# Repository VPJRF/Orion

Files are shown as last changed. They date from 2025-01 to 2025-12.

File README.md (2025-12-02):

# Orion
*Een slim hulpmiddel dat de nachtrust en gemoedsrust van een mantelzorger van een persoon met dementie verbetert, door de nachtelijke oriëntatie in ruimte en tijd en de slaapkwaliteit van de persoon met dementie te ondersteunen.*

*Projectteam: Elias Verdegem; Viktor Fabry*

23/05/2025

`PD` persoon met dementie <br>
`MZ` mantelzorger (bv. partner) <br>
`PZ` professionele zorgverlener <br>
`IZ` informele zorgverlener (bv. familielid)

## Samenvatting

_Dit project richt zich op het probleem van **verstoorde dag-nachtritmes bij mensen met dementie**, wat zowel hun slaap als de nachtrust van hun verzorgers verstoort._

Het probleem is geanalyseerd door middel van **bevragingen en observaties**, waarbij de verschillende aspecten en gradaties zijn geïdentificeerd. Vervolgens is met behulp van **vijf iteraties aan prototypes** onderzocht hoe het zintuiglijke spectrum optimaal benut kan worden om de PD in zijn zelfstandigheid te ondersteunen.

Een combinatie van **visuele en auditieve prikkels** op strategische plaatsen doorheen de nachthal **begeleidt de PD bij een nachtelijk toiletbezoek** en **voorkomt het mogelijks daarop volgende nachtelijke dwalen**.

> ✨ **_Slimme lampjes verlichten de route en vormen oriëntatiepunten._**<br>
> ⌛ **_Een geruststellende herkenbare stem herinnert aan tijd en nachtrust._**<br>
> ❗ **_Bij afwijking wordt de MZ meteen visueel gewaarschuwd._**

Door de hulp kan de PD ’s nachts zijn plan trekken. De MZ kan met een gerust hart doorslapen.

**_Orion_** *belooft zo de zelfstandigheid van mensen met dementie te bevorderen, hun onrust te verminderen en de belasting voor mantelzorgers te verlichten en maakt zo thuiszorg aangenamer en duurzamer.*

<p align="center">
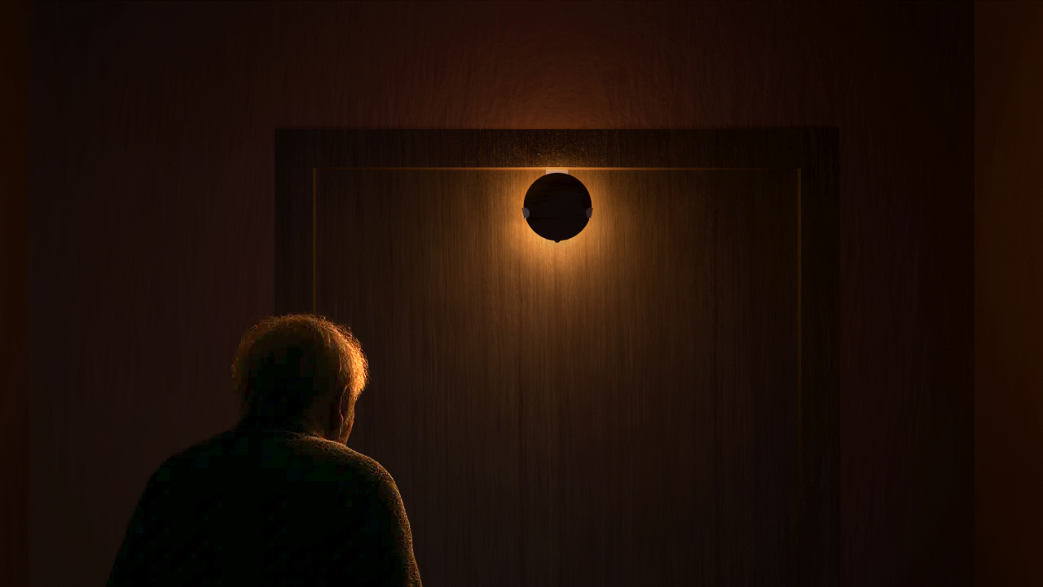
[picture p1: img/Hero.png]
  
</p>

> 🎥 [Ontdek hoe Orion werkt](https://www.youtube.com/watch?v=VIDEO_ID)

## Introductie

> _“Wanneer de nachten te zwaar worden, moeten mantelzorgers [hun partner] loslaten – niet omdat ze willen, maar omdat ze niet meer kunnen.”_ – zorgverlener

Mensen worden steeds ouder. In 2023 in België gemiddeld 82,5 jaar  (PwC, 2024) [^1]. De keerzijde van de medaille is dat hierdoor chronische ouderdomsziektes zoals Alzheimer's vaker voorkomen. **Op vandaag krijgt ongeveer 1 op 5 in de loop van zijn of haar leven een vorm van dementie.** Dementie is een wereldwijd probleem dat 55 miljoen mensen treft en jaarlijks 10 miljoen nieuwe gevallen kent. In België lijden ongeveer 200.000 personen aan een vorm van dementie, en door de vergrijzing wordt verwacht dat dit aantal tegen 2070 zal verdubbelen (Expertisecentrum Dementie, 2021) [^2]. In het toekomstige value based healthcare (VBHC) model (PwC, 2024) [^1] **wordt de zorgverlening verder richting de eerstelijns- en nuldelijnszorg verschoven**. Dit moet onder andere een oplossing bieden aan het groeiende personeelstekort in de gezondheidssector. **Deze evolutie onderstreept het belang van de informele zorgverlener en in het bijzonder de mantelzorger in het geval van zorg voor mensen met dementie.**

**Personen met dementie hebben moeite met een standaard slaappatroon, wat leidt tot nachtelijke onrust en dwalen** (Thomas & Ritter, 2022) [^3]. Dit verstoort niet alleen de nachtrust van de persoon met dementie zelf, maar ook die van hun mantelzorgers, vaak de partner. **Deze aanhoudende belasting kan leiden tot fysieke en emotionele uitputting van de mantelzorger**, wat de beslissing tot een vaste opname in een woonzorgcentrum kan bespoedigen.

**Het doel van dit project is om een oplossing te ontwikkelen die de nachtrust van PD en hun MZ bevordert, zodat thuiszorg langer mogelijk blijft**. Daarbij is het cruciaal om de autonomie van de zorgbehoevende te ondersteunen en de druk op MZ te verlagen. Dit vereist oplossingen die rekening houden met de **uiteenlopende en veranderende cognitieve en zintuiglijke capaciteiten van PD**. De focus ligt op het minimaliseren van nachtelijke interventies en het ondersteunen van een zelfstandig dag-nachtritme. De ontwikkelde oplossing moet bovendien flexibel zijn en ook in een woonzorgcentrum gebruikt kunnen worden om de professionele zorgverleners te ontlasten.

## Methodologie



De methodologie volgt het **triple diamond** ontwerpmodel, bestaande uit vier fasen: **discover**, **define**, **develop** en **deliver**.

In de fase **discover** wordt via een **literature review (N=16)** onderzoek gedaan naar uitdagingen in de zorg voor personen met dementie. Vervolgens vinden **user interviews (N=4)** plaats met mantelzorgers, familieleden en zorgverleners, waarbij gebruik wordt gemaakt van **empathy mapping**. Daarnaast wordt via **ethnography (N=1)** de dagelijkse praktijk geobserveerd in dagverblijf DVC Robijn, afdeling dementie, binnen WZC Sint Eligius. De verzamelde inzichten zijn gestructureerd weergegeven in een **fishbone diagram**, waarbij vooral het verstoorde dag-nachtritme en de daarmee samenhangende belasting voor mantelzorgers naar voren komen als prioritair probleem. Een aanvullend **state of the art**-onderzoek leidt tot het initiële concept van de klinkklok als vertrekpunt voor verdere testen.

Tijdens de **define**-fase worden prototypes iteratief ontwikkeld en geëvalueerd in testwaves, met elk een specifieke focus. In **wave 1** worden **conceptuele prototypes** (klinkklok, vloerlicht, breadcrumbs) onderzocht via **user feedback sessions (N=7)** met mantelzorgers en professionele zorgverleners in Huize Ter Walle, en via **user feedback sessions (N=3)** in DVC Robijn. Nadien wordt een stap teruggenomen met een gerichte **literature review (N=1)** over de problematiek van dwalen en sundowning. In **wave 2** worden de bevindingen toegepast als **feature prototypes** (beacon, breadcrumb, kussen, knuffel) die zich richten op het vaststellen van de featureset via een **evaluation matrix**, met **Wizard of Oz testing (N=3)** bij ouderen met en zonder dementie. Voorafgaand vindt er een ongeplande **user evaluation (N=1)** plaats met een expert in fixatie en valpreventie. De resultaten zijn geprioriteerd volgens de **MoSCoW-methode**, wat resulteert in een productconcept bestaande uit licht en geluid nabij het bed, de slaapkamerdeur en het sanitair, inclusief een feedbacksysteem voor mantelzorgers. Uitdagingen liggen in acceptatie, adaptatie en tijdige implementatie. Opties voor uitbreiding naar andere doelgroepen zijn onderzocht om het product reeds in een vroeg stadium van de ziekte te introduceren.

In de fase **develop** wordt via **CMF prototypes** (vlinderlampjes) de uiteindelijke look & feel bepaald, met behulp van een **interactive survey (N=12)** bij ouderen en ouders van jonge kinderen via **BERT-testing**. In **wave 4** zijn de **UI & UX prototypes** geëvalueerd via **Wizard of Oz testing (N=5)** met het **think aloud protocol**.

De laatste fase **deliver** omvat de evaluatie van volledig autonome prototypes (**wave 5**) als **pilot testing** via een **validation session (N=2)**.

## Discovery

### Doelstellingen

Een goed beeld vormen van wat de ziekte inhoud en de impact op de omgeving.

> ❓**Hoe draag je bij aan het mentaal welzijn van mantelzorgers** door hun tijd besteed aan zorg te optimaliseren?
> -	Welke lasten hebben de grootste impact op de mantelzorgers?
> -	Welke ontlasting heeft de grootste potentiële impact?
> -	Welke technologieën bestaan er?

### Materiaal & methoden

Het onderzoek vat aan met een **literature review (N=16)**. Artikels over het ziektebeeld en technologische vorderingen vormen het referentiekader. In een **technology scan** wordt bestaande technologie verzameld tot een beeld over de “state of the art”. Later in het onderzoek doen ze dienst als **benchmarks** voor de productideeën.

De literatuurstudie wordt gevolgd door **ethnographic fieldwork (N=1)** in de dagopvang in WZC St-Eligius. Het volgen van **a day in the life** van professionele zorgverleners en de gasten verrijkt met **contextual inquiries** worden in **field notes** verzamend. In een **cause-and-effect diagram** diagram worden de conclusies gestructureerd.

Een dieper inzicht in de dagelijkse impact van de ziekte op de naasten in thuissituaties zijn verkregen door **user interviews (N=4)** met eerste- en tweedelijns mantelzorgers. **Habit analysis** van frequente scenario’s en **empathy mapping** van de emotionele impact worden gehanteerd om kerngedachten te capteren.

Om te achterhalen voor welk probleem een oplossing binnen handbereik is, worden de bevindingen in een **feasability-desireabilitydiagram** geordend. Het meest zinvolle probleem wordt in een _how might we_ geformuleerd. **Personas** doen dienst als toetsing tijdens _definition_ fase.

### Resultaten

#### Literature review (N=16)

📄 [Protocol](https://ugentbe-my.sharepoint.com/:b:/g/personal/elias_verdegem_ugent_be/EdiS3hkiKK1MplGdmVTWungBmxVn0FbBp6aX2gbiq4Yjcw?e=3pP9zS)
📄 [Rapport](https://ugentbe-my.sharepoint.com/:b:/g/personal/elias_verdegem_ugent_be/EVpkX9X-c-hKqZcMqP5W1E4BfmoQJAslg8WdfgcqIlADtQ?e=OeRcE2)

Dementie is een complexe ziekte met uiteenlopende symptomen.
-	**Geheugen** en **cognitie** (woordvinding, planning en organisatie, oriëntatie in tijd)
-	**Gedrag** en **karakter** (apathie, agressie, angst, verdriet, kwaadheid)
-	**Functionele tekorten** in het dagelijkse leven (basale activiteiten, complexe activiteiten)

Er is een groeiende erkenning van de waardevolle rol van technologie in de ondersteuning van personen met dementie en hun zorgverleners. De meeste technologieën richten zich op de patiënt zelf.
-	**Communicatie** en **sociale interactie**
-	Fysieke **veiligheid** en **bewegingsvrijheid**
-	**Cognitieve stimulatie** en **geheugenondersteuning**
-	Ondersteuning voor dagelijkse zorgactiviteiten en **zelfredzaamheid**

**Artificiële intelligentie** is een belangrijke trend die hierin nieuwe mogelijkheden biedt. Omwille van de leeftijd en de achteruitgaande cognitieve capaciteiten van het doelpubliek brengt de introductie van nieuwe technologieën enkele belangrijke complexiteiten met zich mee.

#### User interviews (N=4)

📄 [Protocol](https://ugentbe-my.sharepoint.com/:b:/g/personal/elias_verdegem_ugent_be/EcmzMGjfi_pDri7_CiFLg6sBVcVGTVBcUN_csnUy3V1scA?e=q4lqXB)

<p align="left">
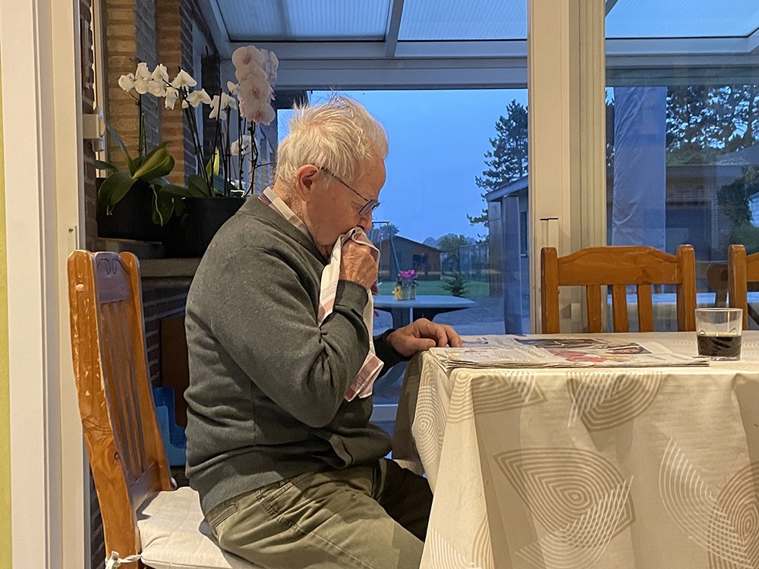
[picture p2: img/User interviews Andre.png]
  
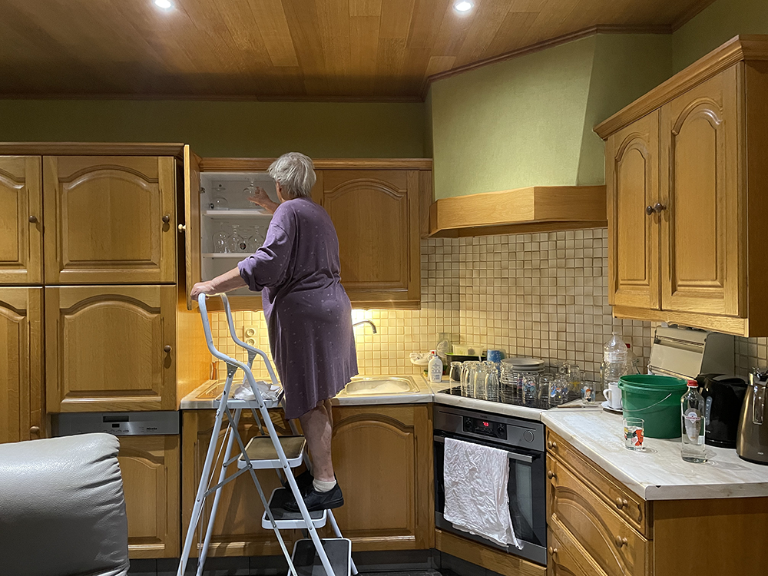
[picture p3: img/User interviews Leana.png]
  
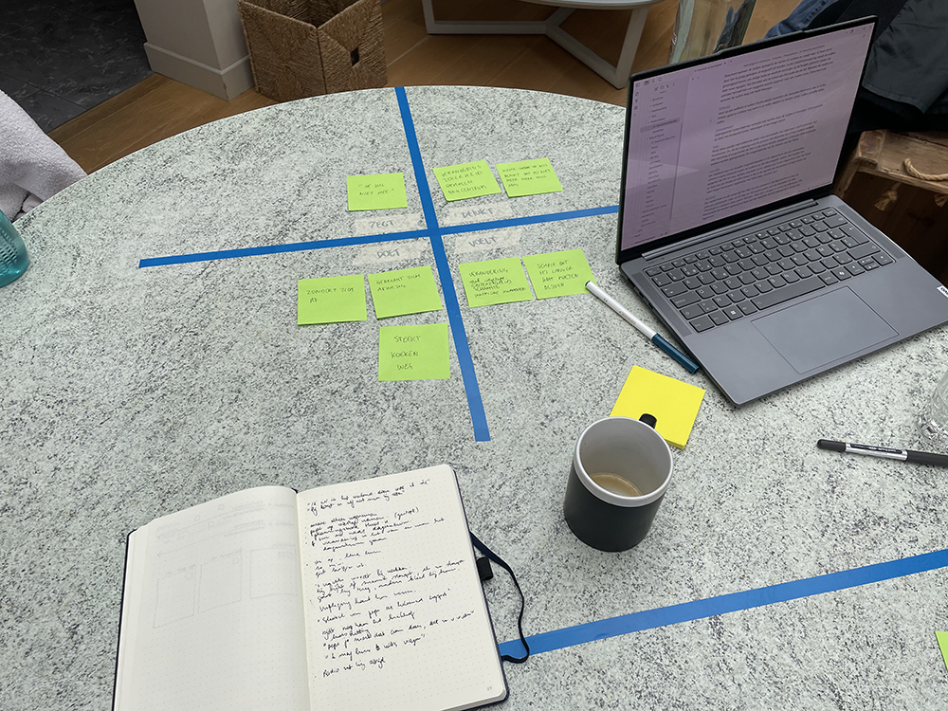
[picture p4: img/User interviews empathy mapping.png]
  
</p>

Wat in de literatuurstudie nog onderbelicht lijkt, maar in de praktijk sterk naar voor komt, zijn de moeilijke nachten.

> _“Zit hij daar midden in de nacht aan de keukentafel, volledig gekleed, z’n krant aan ‘t lezen.”_ – mantelzorger en partner

Mantelzorgers willen de overstap van thuiszorg naar een woonzorgcentrum zo lang mogelijk uitstellen. Uit schrik om gescheiden te zijn, maar ook uit schaamte om te moeten toegeven dat ze het niet meer aankunnen.

> _“Na een week in kortverblijf is hij sterk achteruit gegaan. Sindsdien komt hij er niet meer bij zitten wanneer er bezoek is.”_ – tweedelijn informele zorgverlener (zoon)

#### Ethnography (N=1)

📄 [Protocol](https://ugentbe-my.sharepoint.com/:b:/g/personal/elias_verdegem_ugent_be/EbZtCITc4uJAq0ycfyGaPi8BeBhuUqo_bVPuqhUFXoU3WQ?e=zYbrPR)
📄 [Rapport](https://ugentbe-my.sharepoint.com/:b:/g/personal/elias_verdegem_ugent_be/EUZXoSR17MNIq53AvzIOdvEBZ89_BWPycliHvZ6ZHHcRLg?e=TfPVYO)

<p align="left">
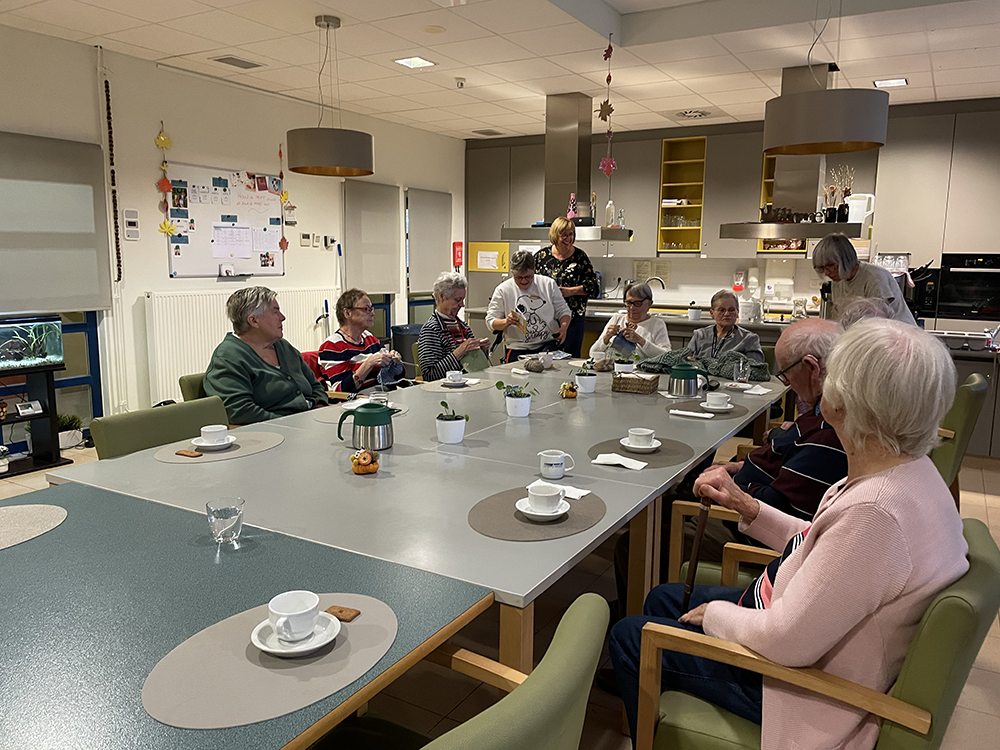
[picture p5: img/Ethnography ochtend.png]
  
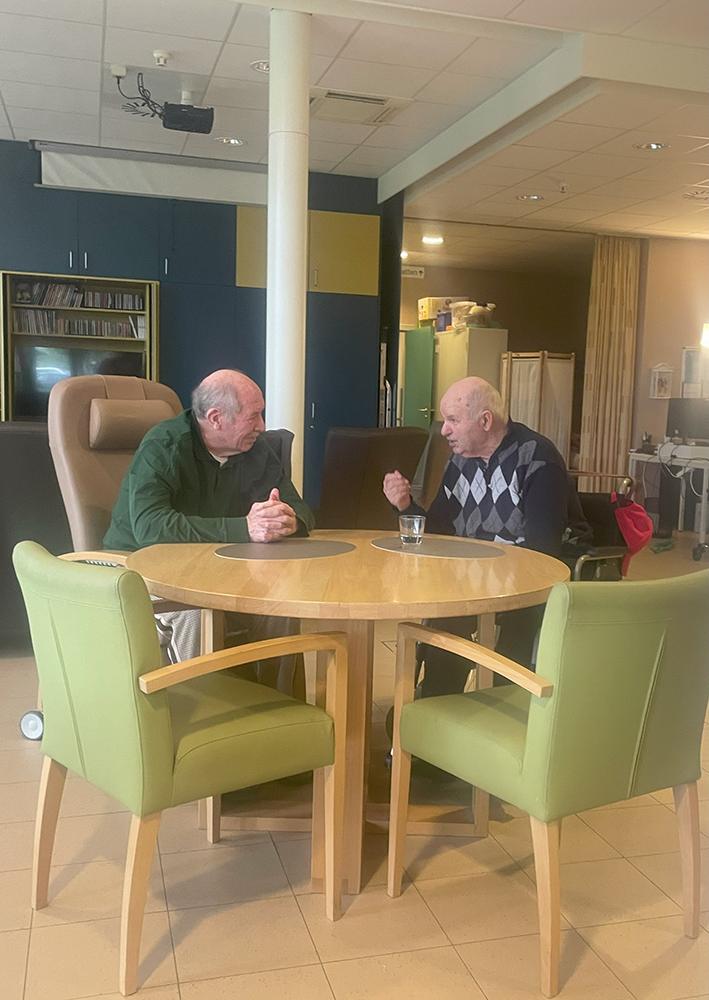
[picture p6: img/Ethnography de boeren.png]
  
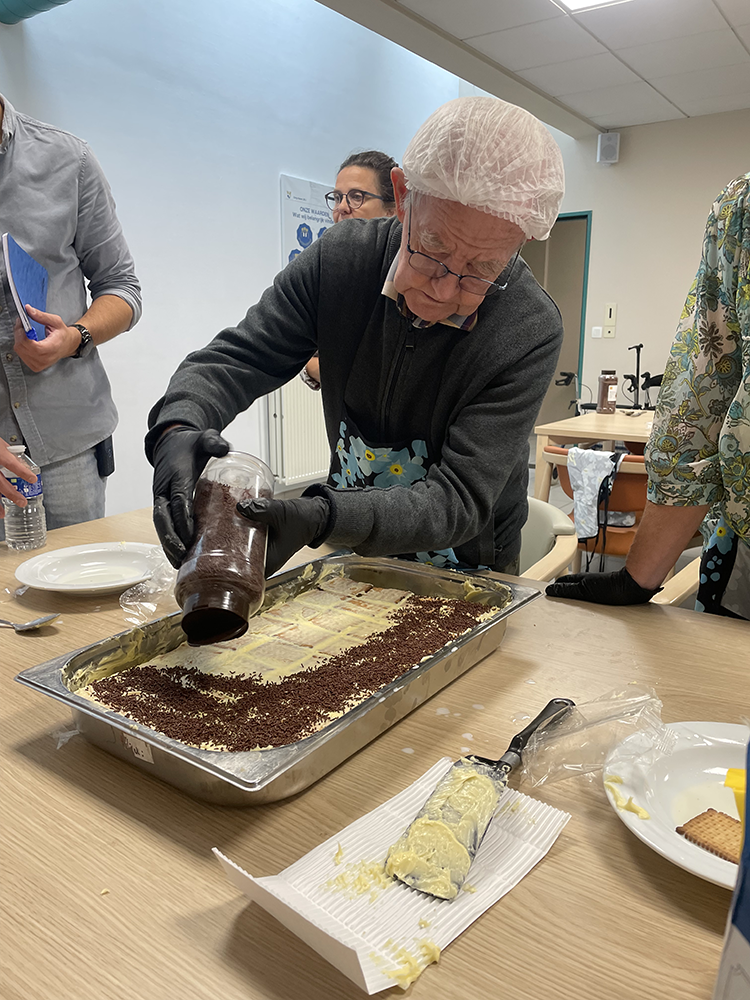
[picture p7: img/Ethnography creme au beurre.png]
  
</p>

Ondanks het personeelstekort wijzen de professionele zorgverleners voornamelijk in de richting van de **mantelzorgers** wanneer het over overbelasting gaat. Ze spelen een cruciale rol doorheen de evolutie van de ziekte. Ze krijgen te kampen met **fysieke**, **emotionele**, **financiële** en **praktische** problemen.
Een gebrek aan **tijd** en **middelen** vormt veelal de onderliggende oorzaak.

> _“Wanneer we dan vragen hoe het met ze gaat, barsten ze in tranen uit.”_ – zorgverlener

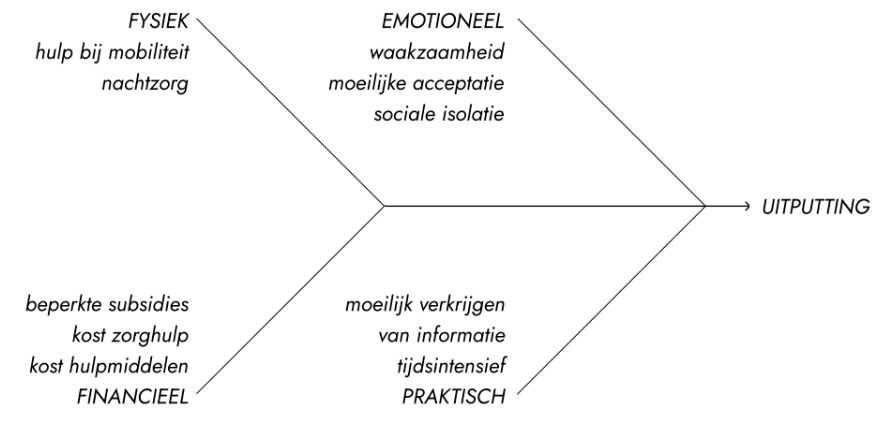
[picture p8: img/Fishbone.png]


Mantelzorgers wijden hun leven vaak volledig aan hun partner met de ziekte toe, ten koste van zichzelf. Liefde ruimt plaats voor gemis, frustratie en schaamte.
Dagcentra of een uitstap met een vrijwilliger of tweede lijn mantelzorger bieden ademruimte. Mantelzorgers hebben deze tijd nodig om van de vaak **korte nachten** en **zware zorgdagen** te recupereren en **sociaal isolement** te vermijden.
<br clear="all">

> _"[…] haar mantelzorger komt haar 's ochtends soms met tranen in de ogen afzetten." ... "Na 16u staat de mantelzorger er opnieuw alleen voor, net wanneer de gasten net heel overprikkeld zijn."_ – zorgverlener

Er is nood aan een oplossing die ook in de overige uren van de dag de autonomie van de zorgbehoevende ondersteunt.
Zowel in woonzorgcentra als in thuissituaties zijn **nachtelijke problemen** zeer uitputtend door de noodzaak voor permanente **waakzaamheid**. **Incontinentie**, **slapeloosheid**, **doolgedrag** en het bijhorende **valrisico** liggen hierbij aan de bron. 

> _"Sommigen zijn het dag-nachtritme volledig kwijt, wat leidt tot doolgedrag. Dan geef je ze slaapmedicatie, maar vergroot hun valneiging."_ – zorgverlener

De zorgbehoevende verhuist vaak stapsgewijs (via **dagverblijf**, **kortverblijf**, **aanleunflat**) van **thuis** naar **vast verblijf**." Dit valt de MZ heel zwaar en introduceert nieuwe verwarring bij de PD door een nieuwe onherkenbare omgeving.

> _”[…] Sociale Dienst merkt dan op dat de mantelzorger het niet meer aankan. […] Ze hebben het gevoel dat ze hun partner dumpen." [...] "Vanaf dan ben je gescheiden.”_ – zorgverlener

### Conclusies & implicaties

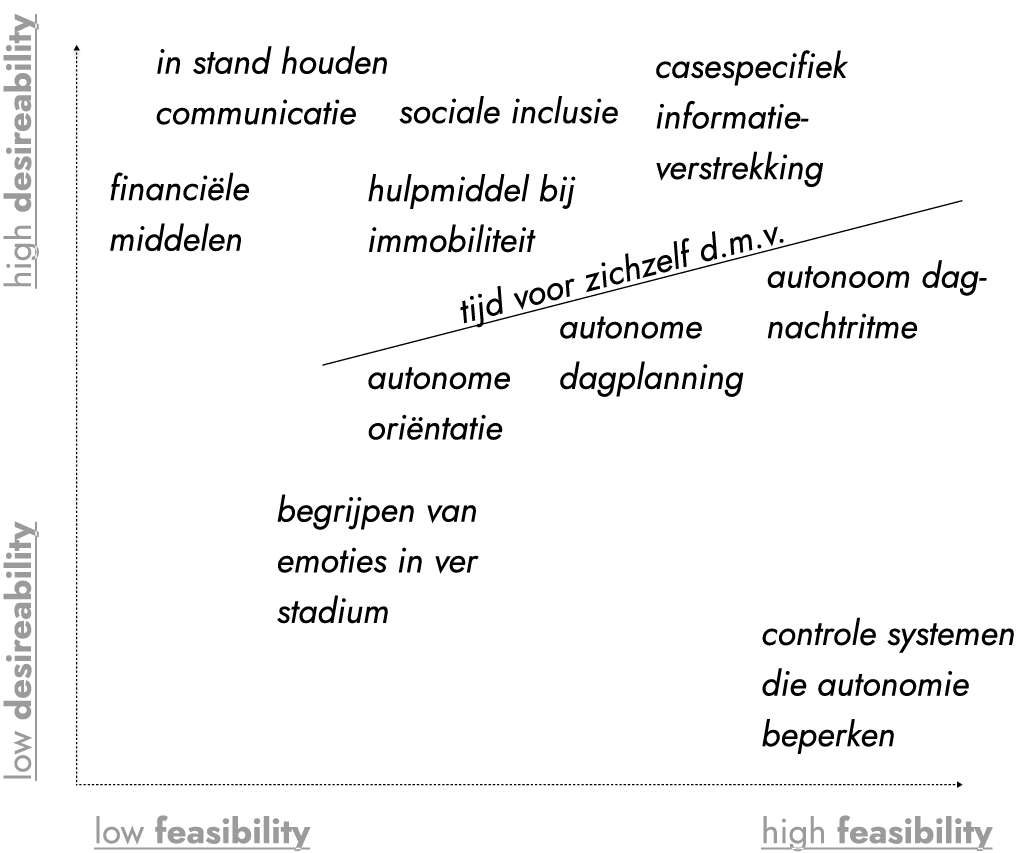
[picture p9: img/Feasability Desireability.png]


MZ van PD dragen een zware, vaak onzichtbare last. Vooral de **nachtelijke zorg** blijkt in de praktijk een cruciale maar onderbelichte bron van uitputting. Het doolgedrag, valgevaar, en het verlies van dag-nachtritme vereisen **permanente waakzaamheid**.

Hoewel bestaande technologieën zich hoofdzakelijk richten op de PD, ligt de **grootste potentiële impact** in oplossingen die de MZ ademruimte gunnen wanneer ze er alleen voor staan. Technologieën die de **autonomie ’s nachts** verhogen en onrust detecteren of vermijden, kunnen niet alleen de draaglast verlichten, maar ook het verblijf thuis aanzienlijk verlengen.

<br clear="all">

>🎯 **_How Might We?_**<br>
> **_Hoe kunnen we ’s nachts de autonomie van personen met dementie ondersteunen en nachtelijke interventies minimaliseren om zo de fysieke en mentale belasting van mantelzorgers te verlichten?_**

<br>

> 📌 **_Design Requirements_**
> - 1\. **Reduceert de noodzaak tot waakzaamheid** en beperkt het aantal nachtelijke interventies van de MZ
> - 2\. **Begeleidt in ruimte en tijd** om aan de zelfstandigheid en eigenwaarden van PD bij te dragen
> - 3\. **Interacties zijn intuïtief en herkenbaar** voor personen met beperkte oriëntatie- of geheugenfunctie
> - 4\. **Reist mee als vertrouwd element** om verwarring bij PD door wijzigende context te verminderen

## Definition I

### Doelstellingen

> ❓ _Hoe draag je bij aan de **nachtelijke zelfstandigheid** van een persoon met dementie?_
> - **Welke situaties** komen het vaakste voor?
> - **Welke interacties** (soort, timing, locatie) zijn intuïtief en behulpzaam?

### Materiaal & methoden

De definition fase wordt gestart met een **design sprint** waarin de **how might we** wordt vertaald in een **innovatrix** en **storyboards**.

Momenteel gebeurt het dat de PD gaat dwalen na op te staan voor een toiletbezoek. De waakzame MZ zal ’s nachts telkens opstaan om de PD opnieuw in slaap te helpen.

<p align="center">
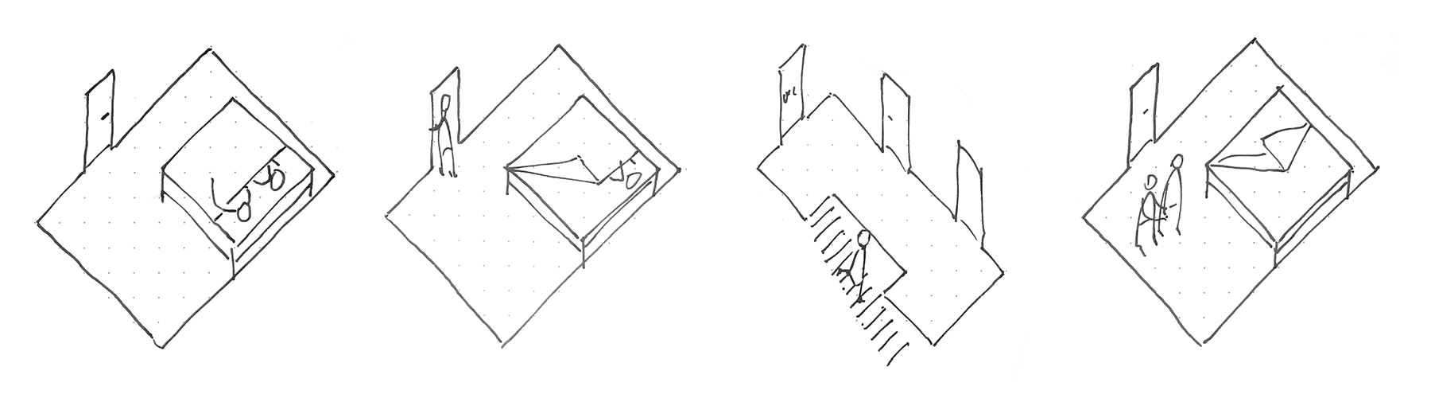
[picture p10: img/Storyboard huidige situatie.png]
  
</p>

De eerste productiteratie is een lichtgevende klink op de slaapkamerdeur. Op basis van kleur wordt onderscheid gemaakt tussen dag en nacht. Een stem biedt tijdgebonden duiding. De klink onderscheidt de kamerdeur van de andere deuren.

<p align="center">
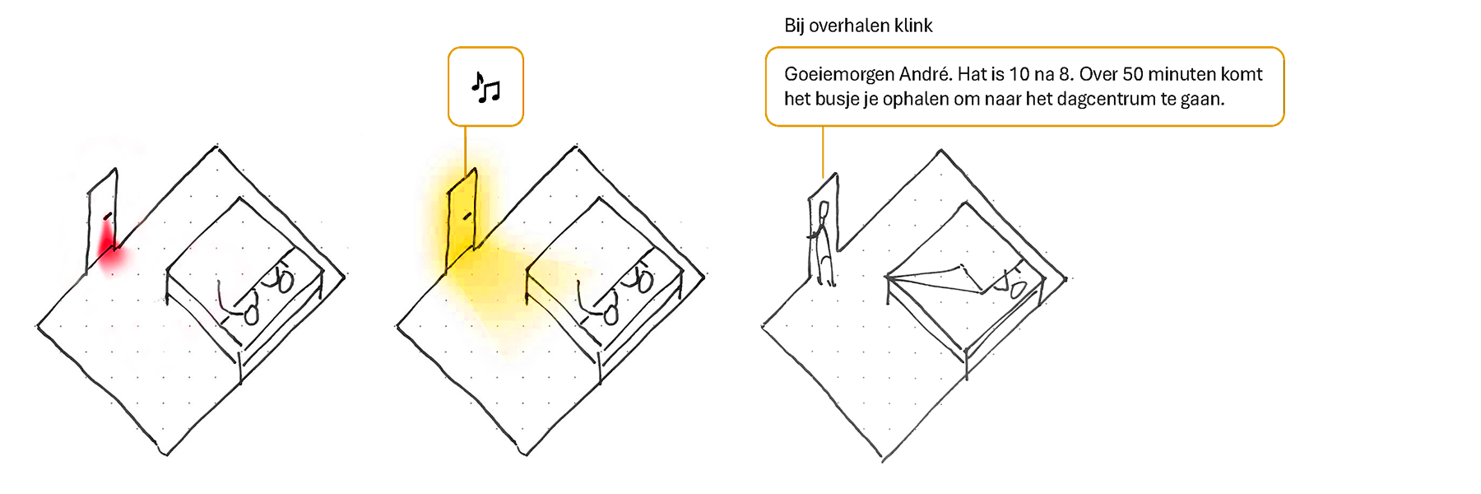
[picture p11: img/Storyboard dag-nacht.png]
  
</p>
<p align="center">
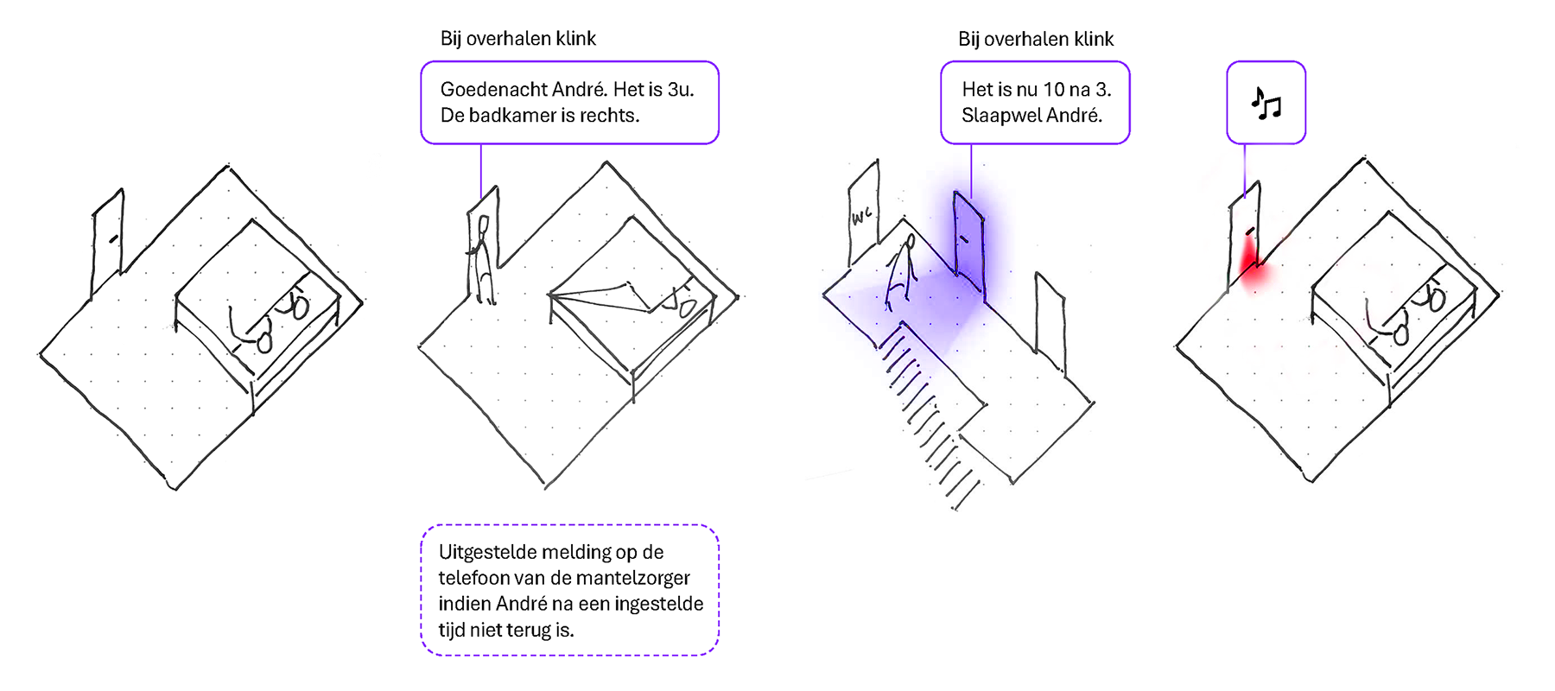
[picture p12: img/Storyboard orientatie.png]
  
</p>

> 🌊 Wave 1 – **conceptuele prototypes** – stimuli
> - **klinkklok**: zoals hierboven beschreven
> - **breadcrumbs**: slimme lichtbronnen die helpen bij veilig en zelfstandig nachtelijk navigeren
> - **vloerlicht**: een vloerdetector die nachtelijk opstaan detecteert en met licht dag-nacht onderscheid maakt en met rustgevend geluid helpt om opnieuw in slaap te vallen

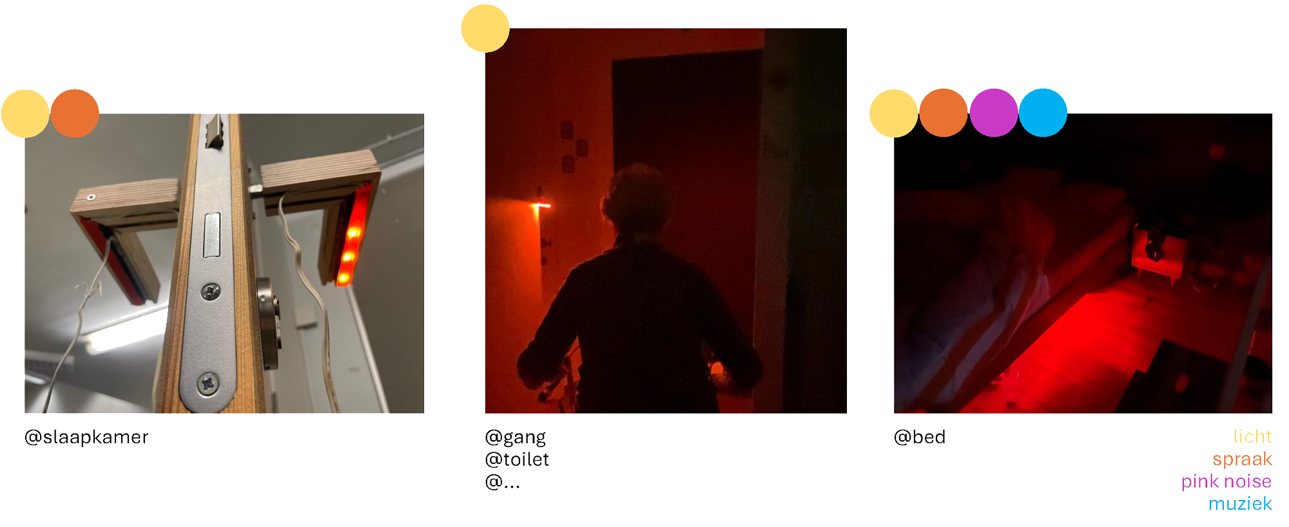
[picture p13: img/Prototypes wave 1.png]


De prototypes worden in een **user feedback sessions (N=10)** in Huize Ter Walle (N=7) en in DVC Robijn (N=3) aan MZs en PZs gedemonstreerd. Er zijn **groepsinterviews** afgenomen en individuele feedback is via een **enquête** verzameld.

### Resultaten

#### User feedback sessions (N=10)

📄 [Protocol](https://ugentbe-my.sharepoint.com/:b:/g/personal/elias_verdegem_ugent_be/EUDGs_sZqw1Cu-SNZ_Z4MUYB4EUygZoMUpzzzmrSuLFlzA?e=GaHmqu)
📄 [Rapport](https://ugentbe-my.sharepoint.com/:b:/g/personal/elias_verdegem_ugent_be/EYPAxhtVcARDhyRcBSE5QyAB_7105NtN1UUdGcgKd0noVQ?e=lRj64M)
📄 [Enquête](https://ugentbe-my.sharepoint.com/:b:/g/personal/elias_verdegem_ugent_be/Ef0tJbKGW_dAtwJForc6fqsBGBC1jhmTAPsUzSV54qDXcQ?e=y3iexh)
📄 [Resultaten](https://ugentbe-my.sharepoint.com/:b:/g/personal/elias_verdegem_ugent_be/ETZRhIU3ZTpDvh90dmZtsAcBM5H1ob_vPhDzmzgHq2v9hA?e=dr1w6v)

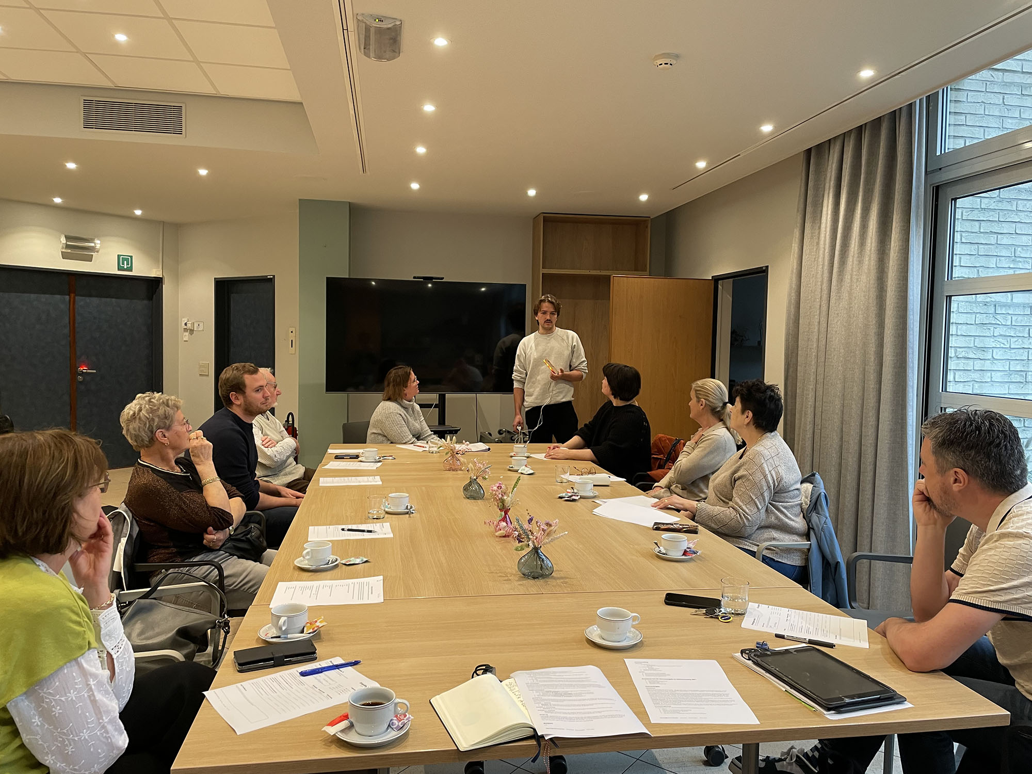
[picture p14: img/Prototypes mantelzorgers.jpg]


De meeste PDs kunnen nog wel kloklezen, maar staan geregeld op voor een **toiletbezoek**, een **glas water** of uit **verwardheid** (_”Ik moet gaan werken in de bakkerij.”, “Ik zoek mijn broer.”_. De MZs beschouwen hun nachtelijk hulp als een noodzaak en een evidentie, met het valrisico als hoofdreden.
> _”Ik ben niet gerust als ik niet mee ga als hij uit de kamer gaat.”_ – mantelzorger en partner

Bij sommigen overheerst de _status quo bias_. Doch blijken MZs zelf creatief in het zoeken naar oplossingen. Nachtelijke oriëntatie wordt ondersteund door **automatische verlichting** en geïmproviseerde **lichtlijnen**. Bij een verminderd tijdsbesef doet een **wake-up lampwekker** met **audioboodschap bij aanraking** dienst.

De cognitieve capaciteit van de PD in thuiszorg varieert sterk. Het **type prikkel is sterk individueel** te bepalen. De prikkel moet intuïtief zijn zoals **een licht of een herkenbare stem**. Kleurcodes zijn te complex.
<br clear="all">

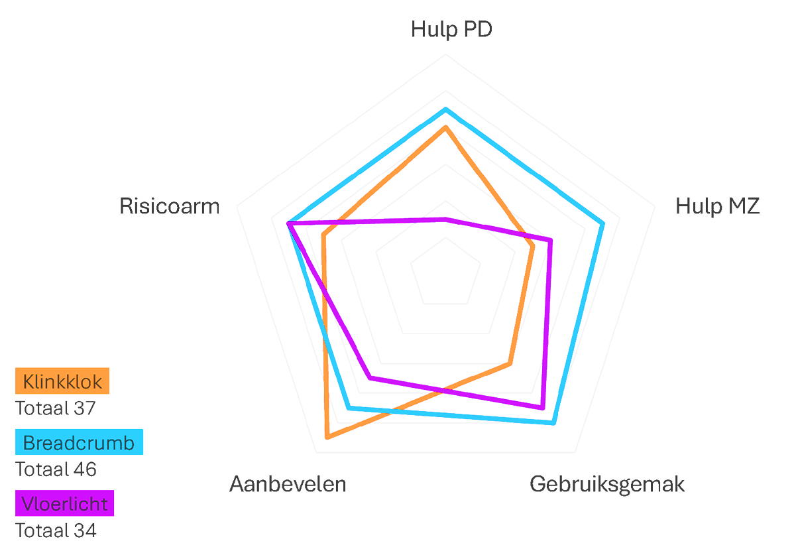
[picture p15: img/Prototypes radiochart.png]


Snoezelgeluiden zijn voor de een storend, voor de ander een slaaphulp. Licht op de deur of onder bed werkt net uitnodigend om op te staan. De prikkel moet zich aan het hoofddoel (het bed) bevinden.

De _breadcrumbs_ komen als winnaar uit zowel de gesprekken, als de enquête. Dit kan worden toegeschreven aan de **intuïtiviteit** (basale aantrekking van licht in ‘t donker), de **autonome werking** (geen complexe interactie en leercurve), de **herkenbaarheid** (domotica), eenvoudige **integreerbaarheid** en het **beperken van storende prikkels in de kamer**.
<br clear="all">

### Conclusies & implicaties

Een **verlichte nachthal** en een hulp bij het oriënteren door een **slimme aansturing** verlaagt het risico op dwalen en vallen. Volledige autonomie van de PD wekt ongerustheid bij MZs. Een adequate **feedback** is dus noodzakelijk.

> 📌 **_Design Requirements_**
> - 1.1. Bezorgt de MZ **feedback over de plaats en duur** van de nachtelijke uitstap
> - 2.1. **Helpt bij oriëntatie naar badkamer of toilet en terug naar bed**
> - 3.1. **Prikkelt gericht naar het hoofddoel** (toilet, kamer, bed)
> - 3.2. Prikkelt in de vorm van **lichtpunten en een herkenbare stem**
>- 3.3. De mee-slapende wordt **gedurende de nacht niet gestoord** door geluiden of licht boven de 5 lux in de kamer

## Definition II

### Doelstellingen

>❓ _Kunnen we het probleem **aan de bron aanpakken**?_
> - Wat veroorzaakt het verstoorde dag-nacht-ritme?
> - Welke doeltreffende oplossingen worden in de praktijk toegepast?

### Materiaal & methoden

Uit de eerste feedback blijkt dat de verstoorde nachtrust uiteenlopende oorzaken heeft, maar de MZs er zelf vaak de vinger niet op kunnen leggen. Een diepergaande **literature review (N=1)** over **dwaalgedrag en _sundowning_** verscherpt het referentiekader.

De bevindingen worden getest in verder uitgewerkte prototypes. De _breadcrumbs_ worden uitgebreid met de _beacon_. Een variant specifiek voor aan bed, met snoezelfuncties en een gerichte led die niet storend is voor de mee-slapende.

> 🌊 Wave 2 – **multisensory prototypes** – features
> - **Beacon**: multisensorieel toestel bij het bed (IR-afstandsbediening)
> - **Breadcrumb**: bewegingsgestuurde lampjes – (IR-afstandsbediening)
> - **Kussen** en **knuffel**: ademhaling simulerende comfortobjecten

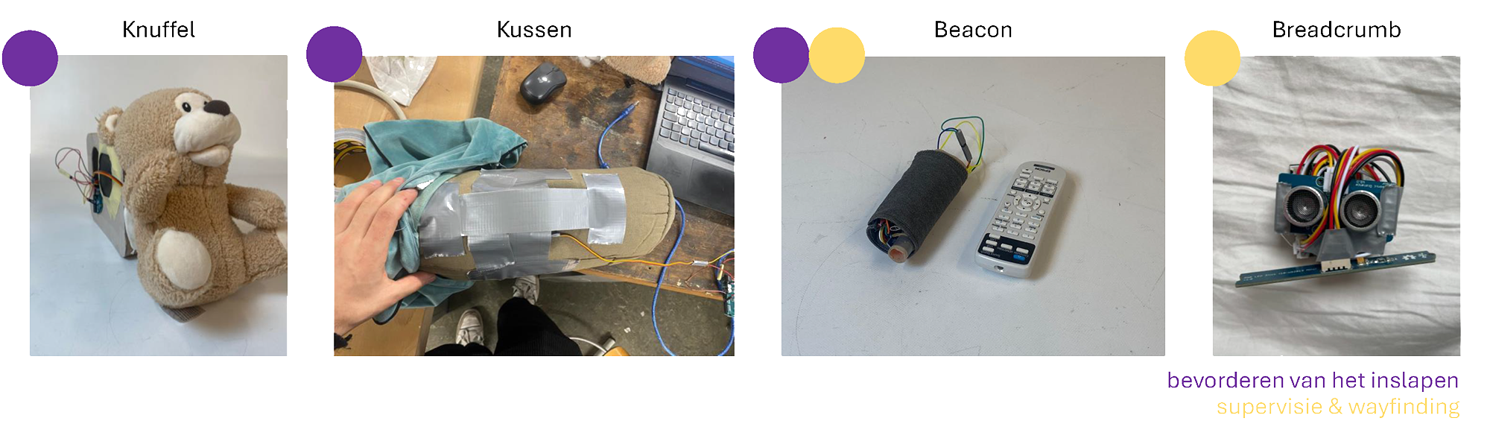
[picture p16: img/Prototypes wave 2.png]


Uit **benchmarks** kan worden geconcludeerd dat er betere varianten van het kussen (_Somnox_) en de knuffel (_Moonie_) op de markt zijn. De geïntegreerde functies worden met **Wizard of Oz testing (N=3)** bij de doelgroep getest. Voorafgaand wordt de werking uitvoerig besproken in een ongeplande **user evaluation (N=1)** met een experte fixatie en valpreventie.
Een **MoSCoW evaluation** helpt de essentie te destilleren.

### Resultaten

> _“Doordat veel ouderen overdag te weinig rust krijgen, zijn ze aan het eind van de dag uitgeteld. […] Ze worden rustelozer, willen naar huis of naar hun ouders, gaan rondlopen, zijn moeilijk gerust te stellen, verwarder en onsamenhangender. […] Het zogenaamde ‘Sundowning’.”_ – Facebookpagina Dementie Anders Beleven

#### Literature review (N=1)

📄 [Rapport](https://ugentbe-my.sharepoint.com/:b:/g/personal/elias_verdegem_ugent_be/EVuqMEwuGKBKsmLIZl0oRTYBc0NNRPol8vBCxzsqA2-cCg?e=P4wvQc)

Het artikel _Wandering and Sundowning  in Dementia_ [^3] onderscheidt drie deelgroepen o.b.v. cognitieve en fysieke capaciteiten. Een **lage cognitieve functie en hoge gedragsverstoringen** vormen het vaakst aanleiding tot dwalen. **Onrust, angst, en waanbeelden** verergeren de neuropsychiatrische symptomen.
- Preventieve maatregelen zijn **meer beweging en zonlicht overdag**.
- Acute maatregelen zijn het voorzien van een **rustige, goed verlichte omgeving** en **aroma- en muziektherapie**.

> 🌊 Aroma en geluid worden toegevoegd aan de _wave 2 prototypes_. De geur van eucalyptus, rustgevende [geluiden]( https://open.spotify.com/playlist/4VAuMb01iWAShef2yUGF71?si=1ebf38cc6ea94c5b) en lichtprojecties creëren een snoezelervaring voor ’t slapen. De geur van koffie vergezelt de lichtwekker.
> Van link naar rechts:
> - Zeebries (snoezel)
> - Ademhaling (snoezel)
> - Zonsopgang (wekker)
> - Alarm (feedback)

<p align="left">
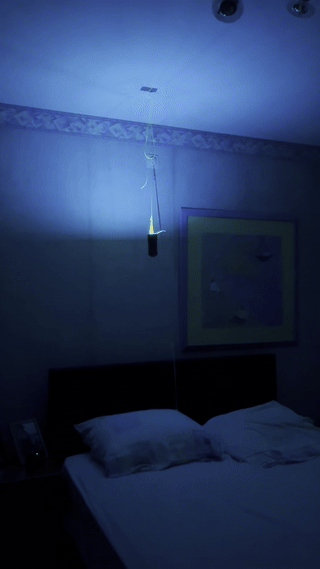
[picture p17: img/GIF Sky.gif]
  
  
  
  
</p>

Bij het _ethnographic fieldwork_ kwam aan bod dat een donkere dorpel door sommige PD als een drempel wordt ervaren. Ook deze paper vermeld _”taping a **2-foot black threshold** in 
front of each door to serve as a visual barrier”_.

#### User review (N=1)

📄 [Rapport](https://ugentbe-my.sharepoint.com/:b:/g/personal/elias_verdegem_ugent_be/EXnrC_QwjRpIjKC0r4nMURQBxLFSH6Xwk91S0IcJtIyq2Q?e=Yyvibq)

Een gesprek met de experte fixatie en valpreventie van WZC St-Eligius geeft inzicht in de werking in een WZC-context.
-	**Spraakberichten** zoals _”het is nog nacht”_ zou de nachtdienst veel werk kunnen besparen. Ook in aanleunflats of thuissituaties waar de PD alleen slaapt, hoeft geluid niet uit de kamer geweerd te worden.
-	In WZC zou **feedback** via **DECT** moeten komen. Een instelbare gevoeligheid is wenselijk. MZs hebben tegenwoordig bijna allemaal een **smartphone**.
-	In WZC kent **aromatherapie** een belangrijke plek. Geuren als **eucalyptus, yland-ylang, sinaasappel en citroen** worden gebruikt voor het bestrijden van nervositeit, angst, boosheid, verwarring, slapeloosheid, etc.

#### Wizard of Oz testing (N=3)

📄 [Protocol](https://ugentbe-my.sharepoint.com/:b:/g/personal/elias_verdegem_ugent_be/EVgxVO37P6NCvh-ebd2gSRIBjbLRaMpq6a8uFbEiW7BVhg?e=qOb3VR)
📄 [Rapport](https://ugentbe-my.sharepoint.com/:b:/g/personal/elias_verdegem_ugent_be/EXnrC_QwjRpIjKC0r4nMURQBxLFSH6Xwk91S0IcJtIyq2Q?e=Yyvibq)

Bij het testen bij PD wordt duidelijk dat de dementiespecifieke features **schaamte en confrontatie** veroorzaken, wat een vlotte **acceptatie in de weg staat**. Een MoSCoW evaluation brengt de functies terug tot licht en spraak.

<p align="left">
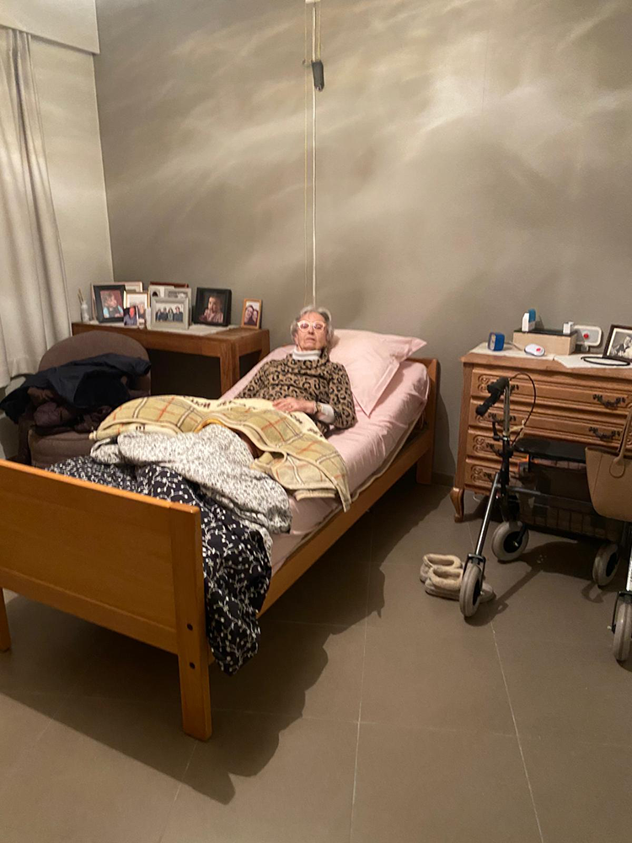
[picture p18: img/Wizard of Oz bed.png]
  
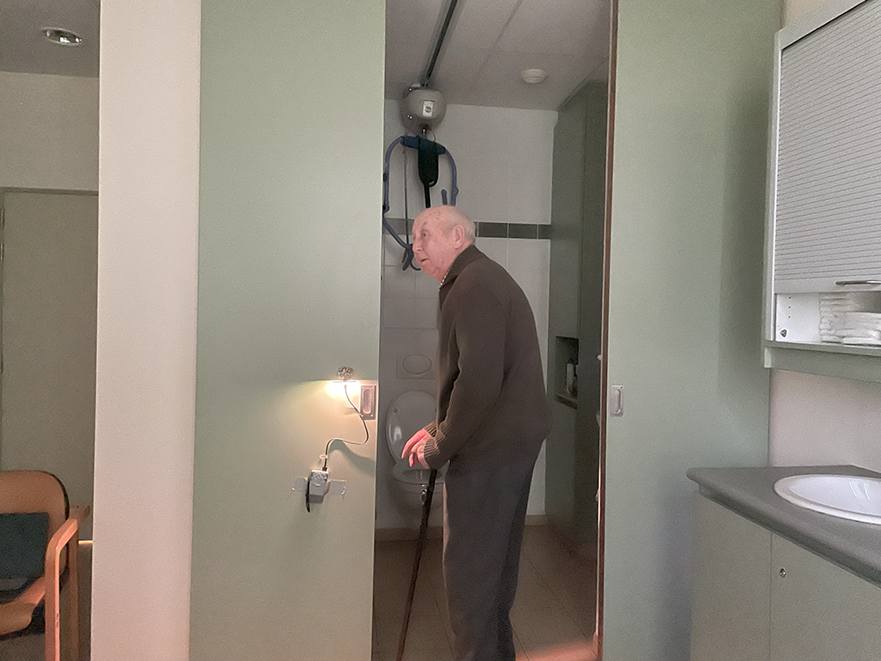
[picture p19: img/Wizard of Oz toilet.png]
  
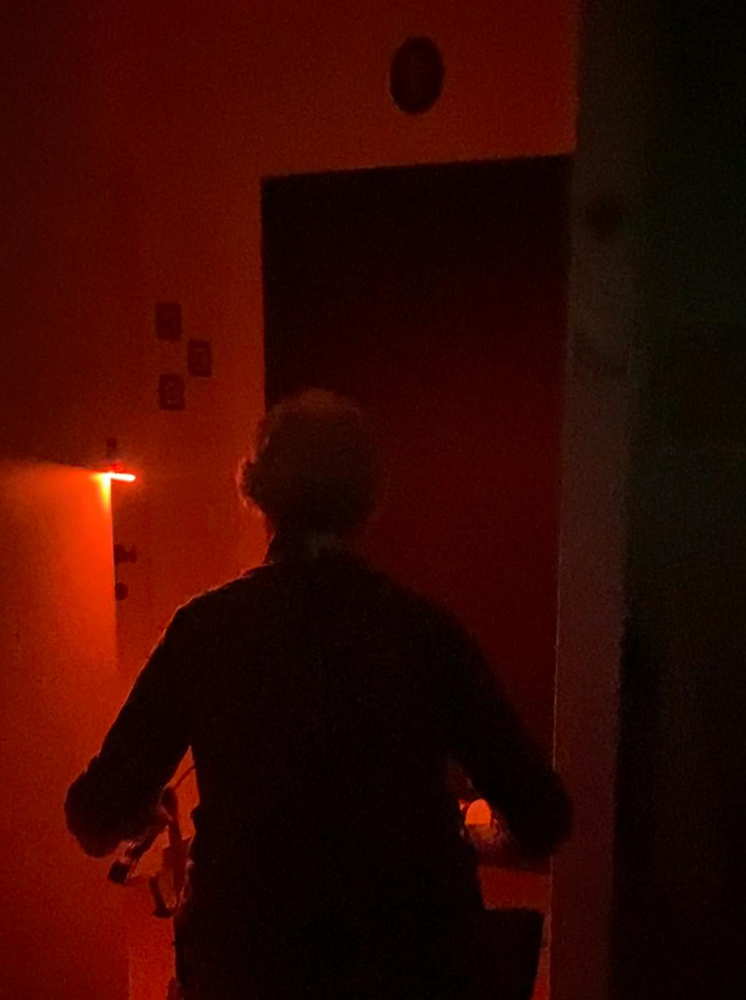
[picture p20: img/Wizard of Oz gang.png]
  
</p>

### Conclusies & implicaties

Symptomen van _sundowning_ in het product integreren leidt tot suboptimale hulpmiddelen, die stigmatiserend kunnen werken, de acceptatie van het basisproduct in de weg staan en de kostprijs onnodig opdrijven. **Spraak, licht en detectie definiëren het _minimum viable product_**. Het beoogde _mental model_ is een routeverlichting en een aangename geheugensteun. De _fluency heuristic_ stelt dat een **geleidelijke introductie van de hulpfuncties** de acceptatie ten goede komt.

> 📌 **_Design Requirements_**
> - 1.2. **Gevoeligheid van de feedback is instelbaar** via een app
> - 3.4. **Hulpfunctionaliteiten zijn instelbaar** via een app
> - 4.1\. **De modules zijn inwisselbaar**, de positie van de geluidsboodschappen is aanpasbaar
> - 5\. Maximale consumentenkostprijs van **€ 150 per module**

<p align="center">
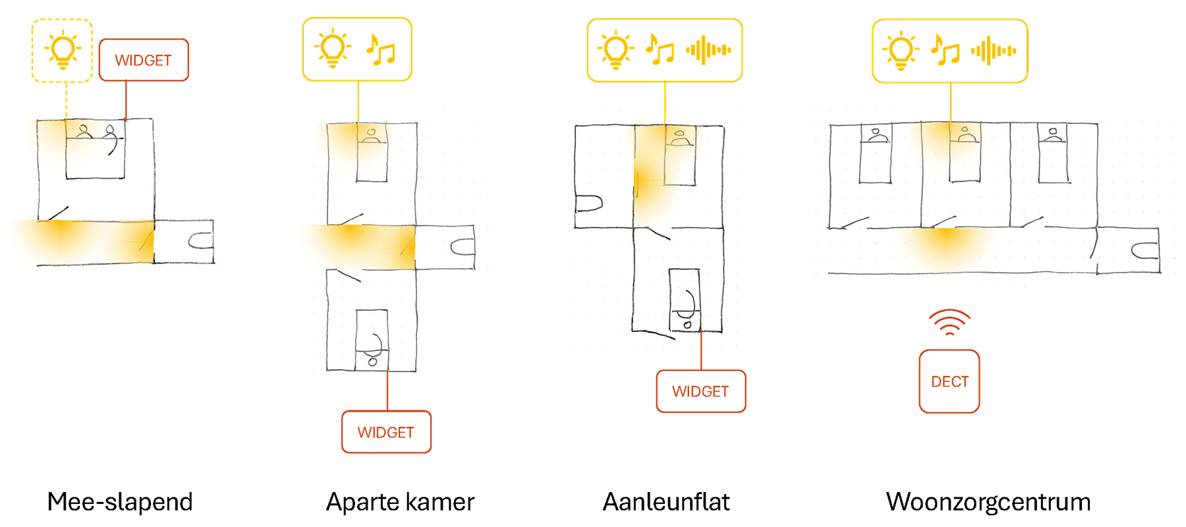
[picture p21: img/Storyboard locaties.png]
  
</p>

Een lichtlijn wordt als variant op de dikke zwarte lijn als barrière geïntroduceerd, door de _breadcrumbs_ van twee vleugels te voorzien.

<p align="left">
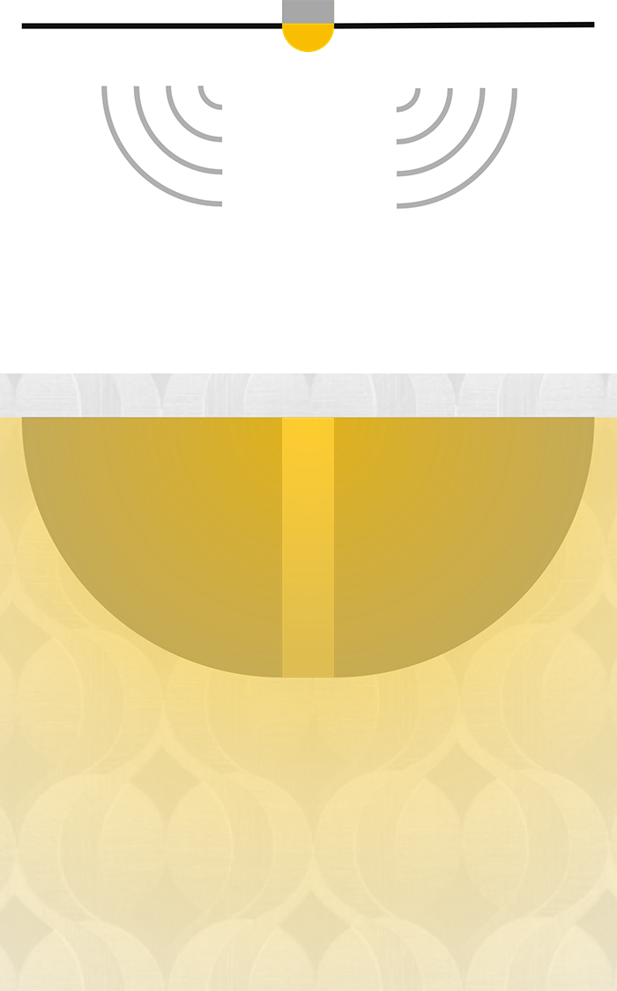
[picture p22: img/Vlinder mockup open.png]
  
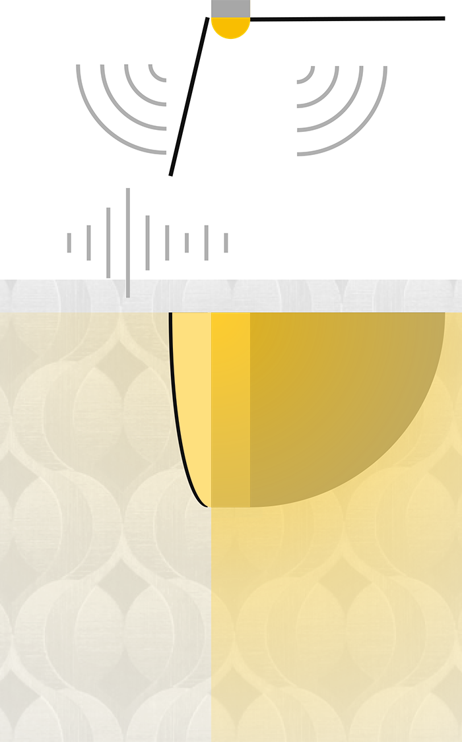
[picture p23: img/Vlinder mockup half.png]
  
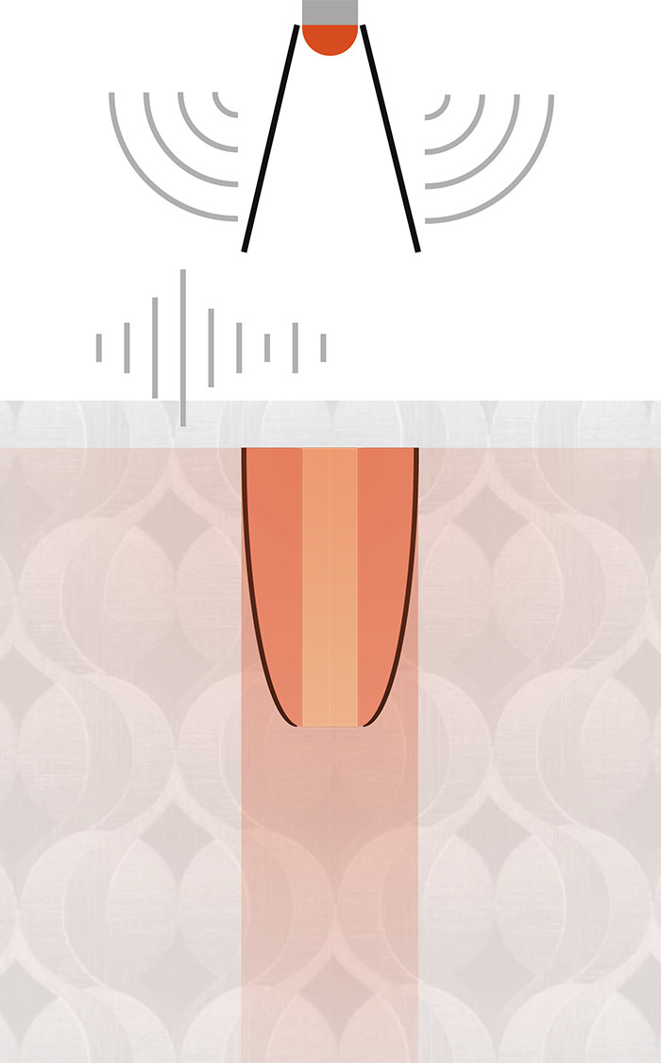
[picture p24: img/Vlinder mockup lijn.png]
  
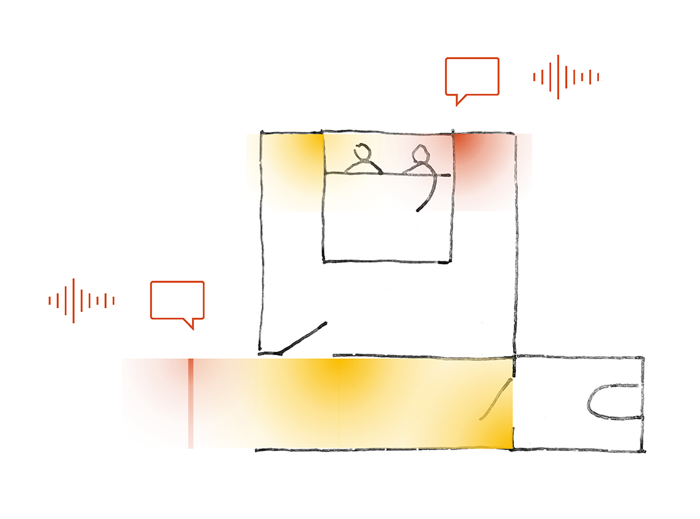
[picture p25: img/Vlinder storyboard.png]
  
</p>

## Develop I – look & feel

 ### Doelstellingen

Er wordt getracht het product **minder stigmatiserend** te maken, door de **doelgroep uit te breiden** en het beter in de omgeving te integreren. Het _MVP_ kan ook voor **ouderen zonder dementie** een hulp zijn. De oriëntatiehulp kan bovendien helpen bij **kinderen (2-4j)** die de babyfoon ontgroeid zijn.   
>❓ _Hoe kunnen we de **acceptie en adaptatie optimaliseren?**_
> - Welke **use-cases** komen in aanmerking?
> - Hoe zijn **look & feel** en doelgroep gerelateerd?

### Materiaal & methoden

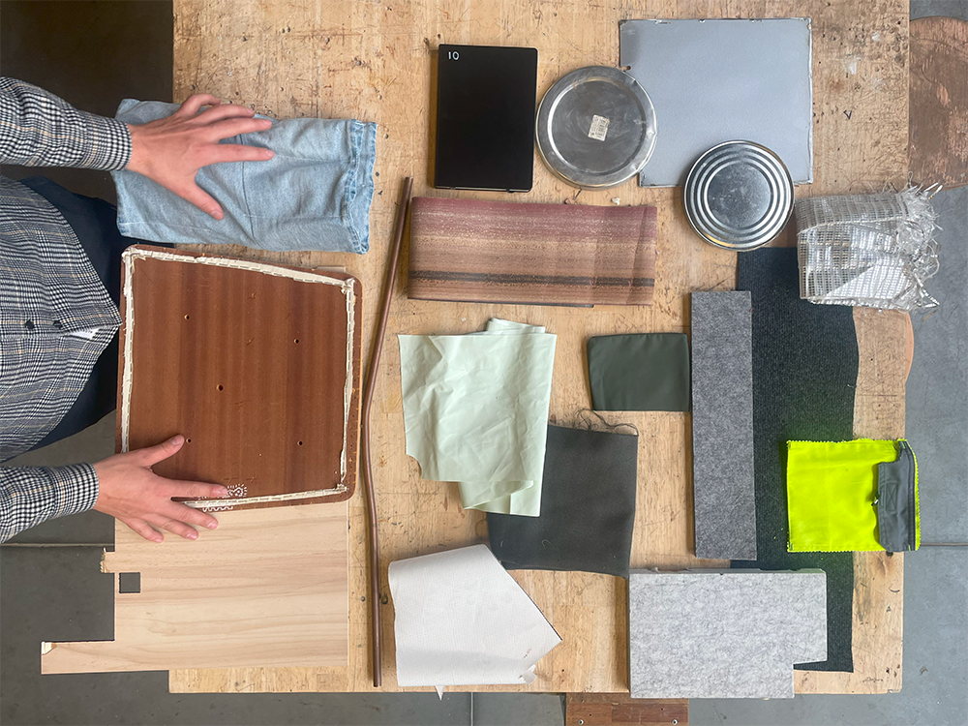
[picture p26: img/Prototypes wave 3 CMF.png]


Bij **scenario thinking** wordt het product denkbeeldig in de alternatieve gebruikscontexten geplaatst. Kinderen, jonge ouders, ouderen en personen met dementie hebben een **verschillend referentiekader** en zullen elk een andere _mental model_ vormen bij eenzelfde _system image_. **Variaties in fijne motoriek, cognitieve capaciteiten en het tweezijdig gebruik** (zorger versus verzorgontvanger) beïnvloeden de _affordances_ en _signifiers_. Variaties in praktische en esthetische voorkeuren beïnvloeden het kleur- en materiaalgebruik. Een [**morfologische matrix**](img/Prototypes%20morfologische%20matrix.png) stuurt de ontwikkeling van de nieuwe prototypevatianten.

<br clear=”all”>

> 🌊 Wave 3 – **CMF prototypes** – look & feel
> - **Boek**: kennis en rust – aardetinten, ruw
> - **Vlinder**: licht, speels en zacht – grijstinten, textiel
> - **Discobal**: futuristisch, opvallend, energiek – fluo color blocking, reflecterend
> - **Schelp**: veilig, clinisch – monochroom, metallic
> - **Pacman**: retro, herkenbaar – natuurlijk, hout

<p align="left">
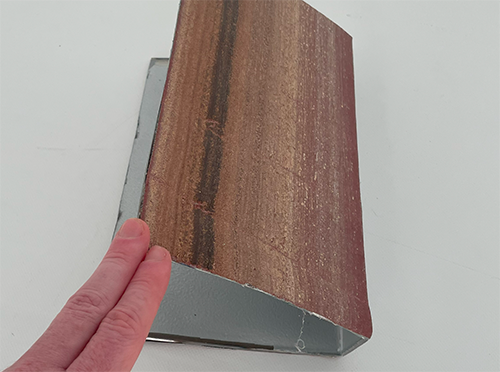
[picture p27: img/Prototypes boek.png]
  
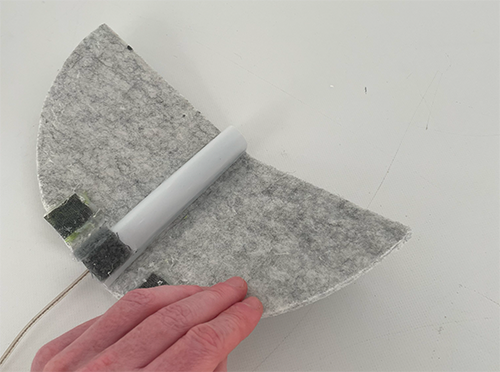
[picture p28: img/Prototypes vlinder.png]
  
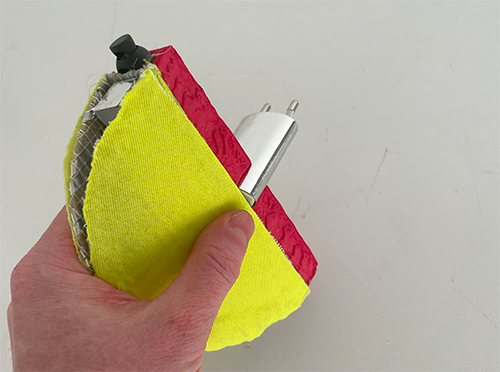
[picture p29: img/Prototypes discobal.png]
  
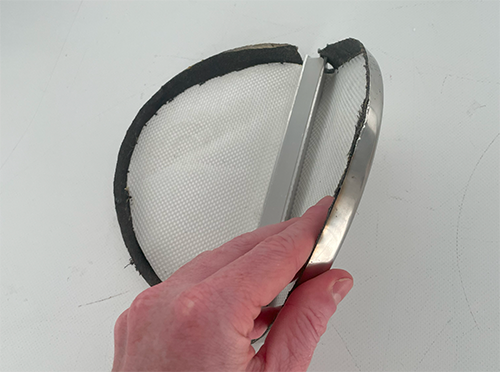
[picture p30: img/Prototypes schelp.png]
  
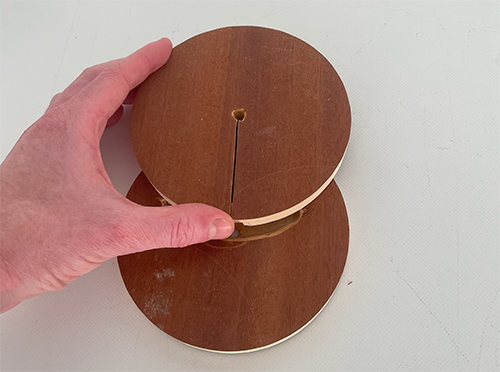
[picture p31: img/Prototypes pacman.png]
  
</p>

Voor elke gebruikscontext wordt telkens bij vier personen de intuïtieve, emotionele reactie op de esthetische kwaliteit bevraagd via **interactive BERT-survey (N=12)**. Tijdens de beoordeling worden vragen over gebruikssituaties en interacties gesteld.

### Resultaten

#### Interactive BERT-survey (N=12)

📄 [Protocol](https://ugentbe-my.sharepoint.com/:b:/g/personal/elias_verdegem_ugent_be/EQc9bVL98C1Bg9wy_j9wrJwBJp-GJjBEg8ULPVaeS8YLjg?e=RuK1Z6)
📄 [Rapport](https://ugentbe-my.sharepoint.com/:b:/g/personal/elias_verdegem_ugent_be/EZvJdp2McdxAnRVUZE21PdMB0frdUHorjLVcXtSo-ZZe9w?e=HnJsfv)
📄 [BERT-enquête](https://ugentbe-my.sharepoint.com/:b:/g/personal/elias_verdegem_ugent_be/Ef-kFxQShQdNrK5ER4mzfosBrSAzOw-ppaQV2JV5mDE-QA?e=NEIaNG)



**CMF**
-	De **houten, ronde vorm** van _pacman_ is het meest prototypische **interieurobject**.
-	Ouders hechten belang aan **stevigheid en reinigbaarheid**.
-	Enkel **kinderen verkiezen felle kleuren**.

**Context**
-	**Mobiele of geïntegreerde toestellen** genieten de voorkeur aangezien er vaak geen geschikte stopcontacten beschikbaar zijn.

**Gebruiksgemak**
-	Ouderen 75+ waarderen **eenvoudige aan/uit besturing** met duidelijke _signifiers_ zoals **fysieke knoppen**. Ze hebben moeite met onvoorspelbare automatische functies.

**Cognitie en emotie**
-	Licht en geluid werken ook bij kinderen geruststellend en oriënterend.
-	Kinderen scannen hun volledige omgeving, waar bij **ouderen de blik naar beneden** is gericht.<br clear=”all”>

### Conclusies & implicaties

Het **interieurobject** moet **robuust**, **hygiënisch**, **subtiel** en **personaliseerbaar** zijn. De **interactie intuïtief en eenvoudig** met een **fysieke aan/uit schakelaar**. Een module is **mobiel** en **onafhankelijk van stopcontacten**.

> 📌 **_Design Requirements_**
> - 4.2. Laat **verplaatsing zonder gereedschap** naar een nieuwe context toe
> - 6\. Laat **plaatsing en configuratie** door ouderen 75+ toe
> - 7\. Bestaat uit **metaal, hout en/of plastic**
> - 7.1. Komt in **3 esthetische varianten**

## Develop II – UI & UX

 ### Doelstellingen

Het verfijnen van de **fysieke, cognitieve en sensoriële ergonomie** en het bepalen van de _affordances_ en _signifiers_ met de focus op gebruik en begrip.
> ❓ **Wat maakt de interactie (UI) en ervaring (UX) aangenaam, doeltreffend en niet-intrusief?**

### Materiaal & methoden

De visuele en auditieve ergonomie wordt met **Wizard of Oz (N=3)** getest met een BLE-bediend UX prototype. Voor de fysieke interacties wordt een UI mockup gebruikt. De _ecological validity_ wordt gegarandeerd door de toestellen in een donkere omgeving op de deur of naast het bed te plaatsen. Een **moodboard** dient als leidraad voor de look & feel.

<p align="center">
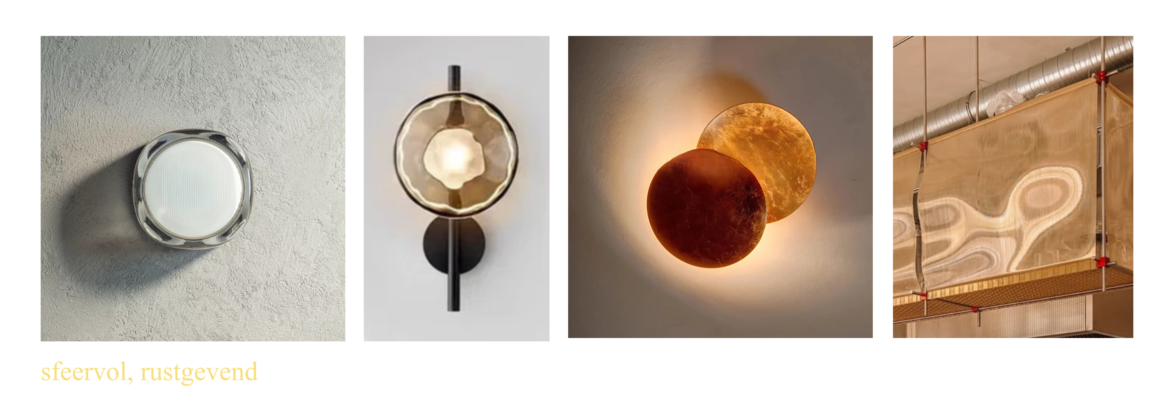
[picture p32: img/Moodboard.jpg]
  
</p>

> 🌊 Wave 4 – **UI & UX prototypes** – comfort & gebruiksgemak
> - **UI mockup**: aan/uit bediening
> - **UX bluetooth remote**: licht- en geluidsspecificaties

<p align="left">
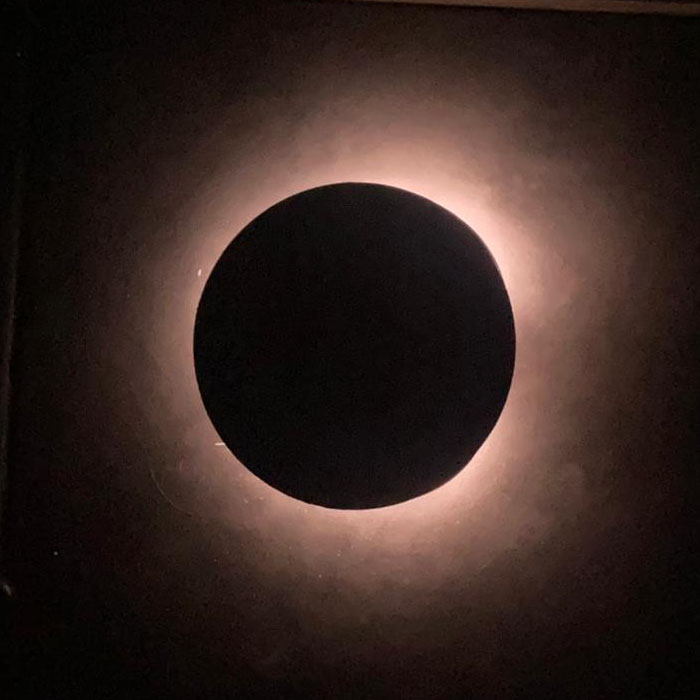
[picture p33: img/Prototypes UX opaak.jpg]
  
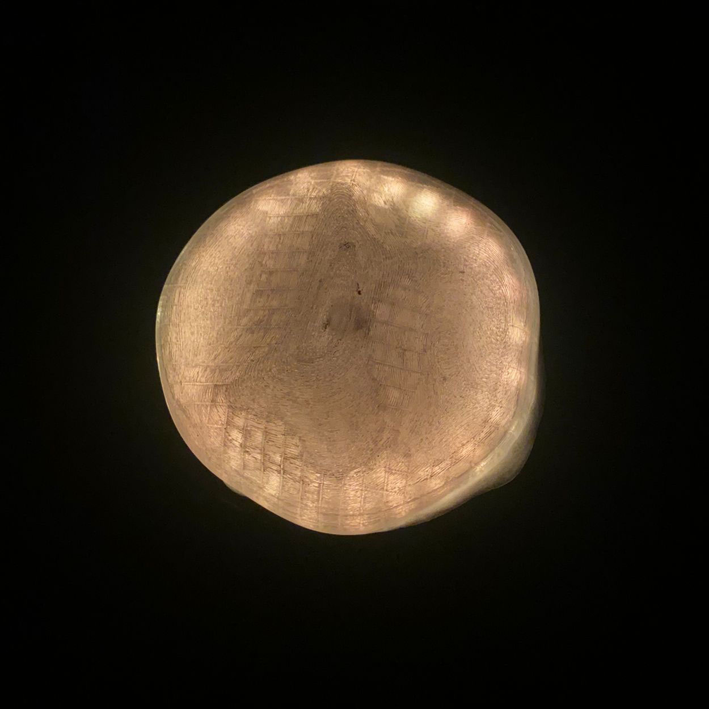
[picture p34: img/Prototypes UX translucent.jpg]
  
  
</p>

Via het **think-aloud protocol** kunnen  _the gulfs of evaluation_ bij de gebruiker met het beoogde effect worden vergeleken. De resultaten zijn samengevat in een [**feature matrix**](img/Prototypes%20UI%20options.png).

### Resultaten

#### Wizard of Oz testing (N=3)

📄 [Protocol](https://ugentbe-my.sharepoint.com/:b:/g/personal/elias_verdegem_ugent_be/EbpEEQu65s1MsOD6PxRYUmsBMa9nkP9GNjpH73FM9u82Bg?e=3dqR0F)
📄 [Rapport](https://ugentbe-my.sharepoint.com/:b:/g/personal/elias_verdegem_ugent_be/EaTvNlM5hxRDjElFE4yJdeABiT8zmxKg7SMp7_JgvvWh1Q?e=RHhe7Z)
🔗 [Testing WebUI](https://eaverdeg.github.io/)

**Visuele ergonomie**
-	Een **translucente kap** maakt het naast het bed gepositioneerde toestel potentieel **geschikt als leeslamp**.
-	Indirecte verlichting bij de **matte kap voorkomt verblinding** in de hal.

**Fysieke ergonomie**
-	De trekschakelaar voldoet aan het _mental model_ van nachtverlichting bij ouderen, maar de PD kan het toestel onbedoeld uitschakelen.
-	Een **voldoende grote**, voor de PD **verborgen wipschakelaar** geniet de voorkeur. 

**Auditieve ergonomie**
-	**Duidelijkheid** en **herkenbaarheid** zijn cruciaal voor gehoorcomfort.

**Cognitieve ergonomie**
-	De **rode** waarschuwingsanimaties evoceert het **brandalarm-metafoor** en werkt onrustwekkend.
-	De **timer-animatie** communiceert helder en genuanceerd aan de hand van een **klok-metafoor**.

<p align="left">
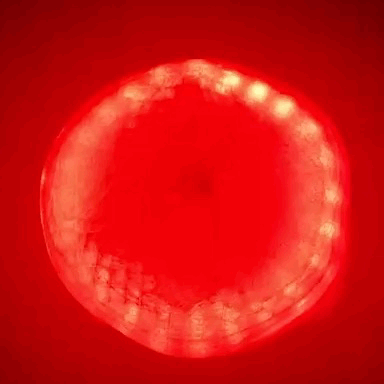
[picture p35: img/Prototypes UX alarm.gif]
  
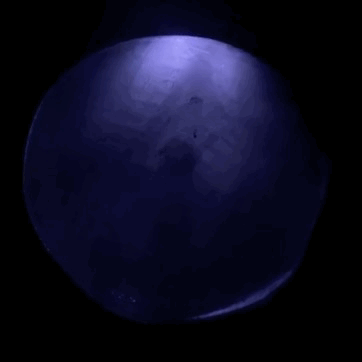
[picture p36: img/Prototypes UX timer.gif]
  
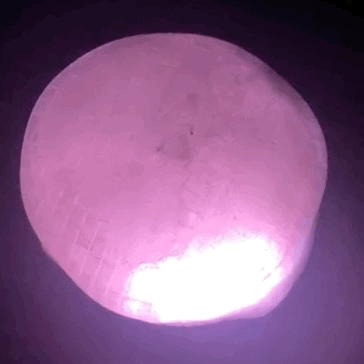
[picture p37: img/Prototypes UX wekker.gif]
  
</p>

### Conclusies & implicaties

Het type licht (direct of indirect) is afhankelijk van de positie. De aan-/uit-bediening is eenvoudig voor de MZ maar verborgen voor de PD. Geluidsboodschappen hebben een grote invloed op de acceptatie en zijn sterk situatiegebonden. De feedback aan de MZ is op niet-alarmerende wijze voorzien.

> 📌 **_Design Requirements_**
> - 1.3. Geeft feedback via een **klokanimatie**.
> - 3.4. **Lichtintensiteit is instelbaar** van 5 tot 50 lumen.
> - 3.5. Wordt geleverd met **drie standaardgeluiden** en de mogelijkheid tot een **eigen opname**.
> - 7.2. Afdekkap komt in een **matte en translucente** variant.

## Deliver – proof of concept

### Doelstellingen

Een _proof of concept_ door het verwerken van de producteisen in een volledig functioneel prototype om met de hoogst mogelijke _ecological validity_ te testen bij de werkelijke eindgebruiker.

> ❓**Vervult het product de vooropgestelde _How Might We_?**
> - Wat zijn de **limitaties** van het product?
> - Welk **verder onderzoek** is noodzakelijk?

### Materiaal & methoden

Met behulp van enkele **cognitive walkthroughs** wordt een **behaviour flow** opgemaakt als blueprint voor de **system architecture**. De installatie werkt autonoom via wifi-connectie met een _Raspberry Pi_ en is opgesteld bij een PD en MZ thuis. De werking is vooraf doorlopen en is vervolgens een volledige nacht actief gebleven voor een **validation session (N=2)**. Na afloop is de MZ geïnterviewd over de bevindingen.

> 🌊 Wave 5 – **proof of concept prototypes** – effectiviteit & intuïtiviteit
> - **Drie geautomatiseerde lampen**: Arduino IoTs communiceren PIR- en GYRO-detectie via het MQTT-protocol met een Raspberry Pi die via state switching de leds en speaker aanstuurt. Zie technische beschrijving.

### Resultaten

#### Validation sessions (N=2)

📄 [Protocol](https://ugentbe-my.sharepoint.com/:b:/g/personal/elias_verdegem_ugent_be/Eba2SJnz_qJLk0D3Vfa5ZnQBhl0F5f7rrHB8iqlQefb_Kw?e=W9rya8)
📄 [Rapport](https://ugentbe-my.sharepoint.com/:b:/g/personal/elias_verdegem_ugent_be/EYsSF-ocI9BGpibg7Vrg9c0BDqhcAzFuGdlTmi8KfnNLWw?e=21pjaG)

*Testpersoon 1 – Zelftest (onderzoeker)*

De test werd uitgevoerd bij daglicht in een verduisterde woning. Alle componenten functioneerden technisch correct en het systeem trok op gepaste wijze de aandacht via licht en geluid. De gyro op het toilet bleek echter overgevoelig, wat leidde tot voortijdige activatie van de geluidsboodschap. De routeverlichting werd als duidelijk en subtiel ervaren.

<p align="center">
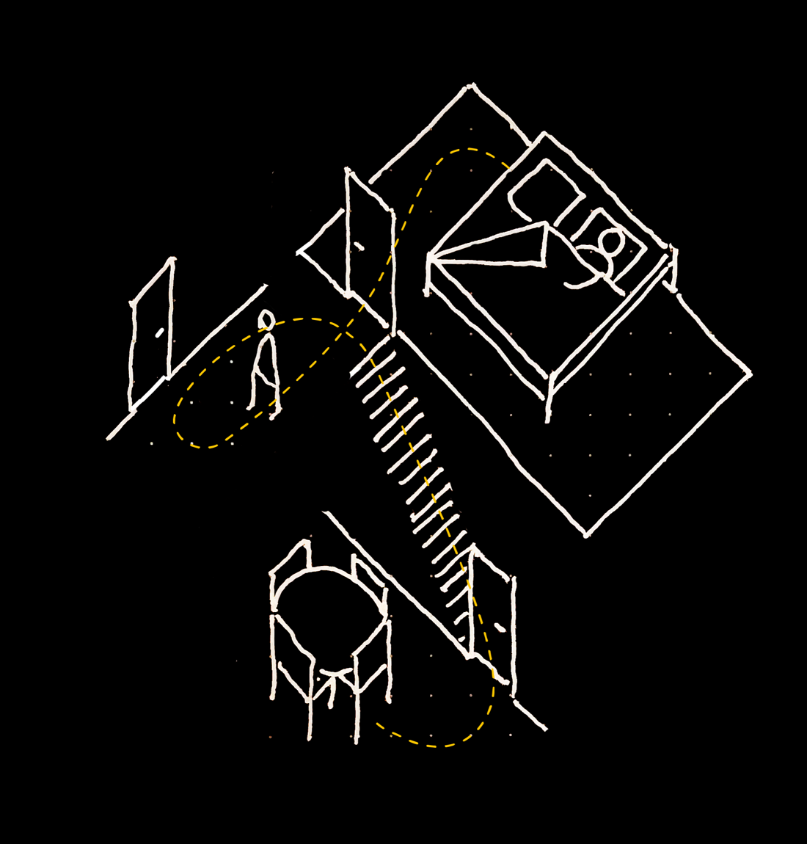
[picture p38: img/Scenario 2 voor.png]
  
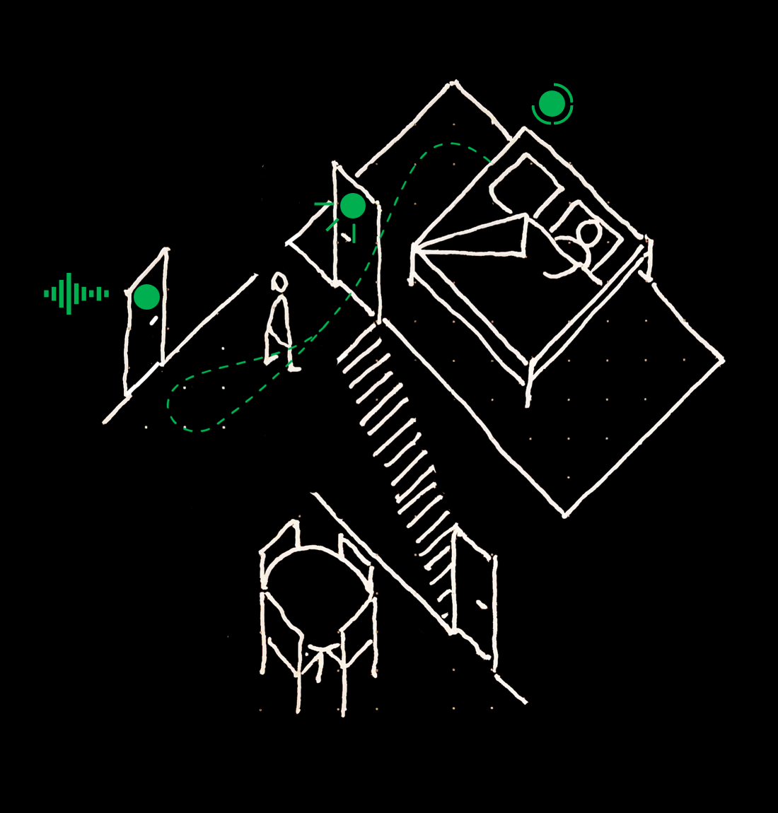
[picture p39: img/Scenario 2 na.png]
  
</p>

*Testpersoon 2 – Persoon met dementie + mantelzorger*

Overdag werkte het systeem correct. Bij de nachtelijke test volgde het systeem de verwachte volgorde niet, ondanks correcte detectie bij het opstaan. Vermoedelijk is een foutieve triggering of plaatsing van de kamerdeursensor de oorzaak. De MZ gaf aan positief te zijn over het systeem en het potentieel te zien, mits verdere aanpassing aan hun specifieke situatie:

- Toilet bevindt zich op een ander verdiep

- MZ wil altijd gewekt worden bij nachtelijke activiteit van de PD

- Huis bevat reeds veel nachtverlichting – vraag naar extra breadcrumbs

<p align="center">
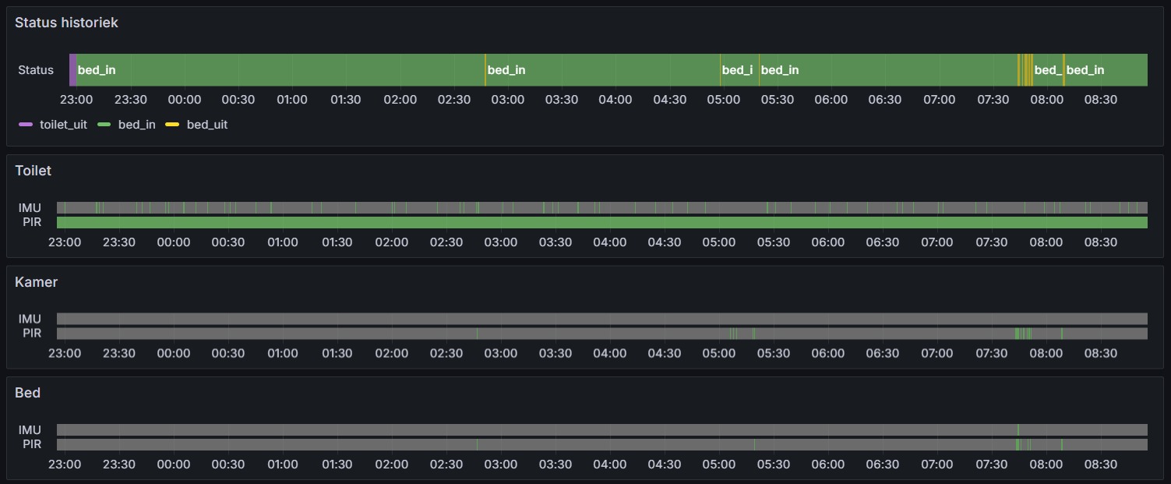
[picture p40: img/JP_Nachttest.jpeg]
  
</p>

<p align="center">
  
  
</p>

**Gedragsobservatie & nabespreking**

Via het *think-aloud protocol* werd vastgesteld dat de interactie intuïtief verliep. Er was geen sprake van verwarring of overbelasting. De MZ waardeerde de autonomie die het systeem kan bieden, maar onderstreepte het belang van betrouwbaarheid en aanpasbaarheid. Er was geen negatieve reactie op licht of geluid.

### Conclusies & implicaties

Het systeem is intuïtief, maar nachtelijke betrouwbaarheid moet beter. Modulair ontwerp en instelbare functies zijn cruciaal. MZ-waarschuwing is noodzakelijk.
Er is een potentiële markt voor het product, mits verdere personalisatie naargelang specifieke situaties van mantelzorgers.

> 📌 **_Design Requirements_**
> -  Modules per ruimte configureerbaar
> -  Instelbare sensorgevoeligheid
> -  Mantelzorgermelding bij activiteit
> -  Extra breadcrumb-verlichting mogelijk
> -  Scenario-templates voor eenvoudige setup

## Conclusie

**_Orion_** is een nachtroutinetool die de zelfstandigheid van personen met dementie ondersteunt en mantelzorgers ’s nachts ontlast. Door visuele en auditieve prikkels strategisch in te zetten, helpt het systeem nachtelijk dwalen te voorkomen en de slaapkwaliteit te verbeteren. De oplossing is tot stand gekomen via diepgaand veldonderzoek, iteratieve prototyping en gebruikerstesten in realistische contexten. **Het eindresultaat is een flexibel, intuïtief en minimalistisch hulpmiddel dat in verschillende zorgomgevingen inzetbaar is**. _Orion_ toont zo aan hoe technologie empathisch kan bijdragen aan duurzame thuiszorg.

<p align="left">
  
  
</p>

> 📌 **_Design Requirements_**
> - 1\. **Reduceert de noodzaak tot waakzaamheid** en beperkt het aantal nachtelijke interventies van de MZ
>   - 1.1. Bezorgt de MZ **feedback over de plaats en duur** van de nachtelijke uitstap
>   - 1.2. **Gevoeligheid van de feedback is instelbaar** via een applicatie
> - 2\. **Begeleidt in ruimte en tijd** met als doel aan de zelfstandigheid en eigenwaarden van PD bij te dragen
>   - 2.1. **Helpt bij oriëntatie naar badkamer/toilet en terug naar bed**
> - 3\. **Intuïtieve, herkenbare interacties** voor personen met beperkte oriëntatie- of geheugenfunctie
>   - 3.1. **Prikkelt gericht naar het hoofddoel** (toilet, kamer, bed)
>   - 3.2. Prikkels in de vorm van **lichtpunten en een herkenbare stem**
>   - 3.3. De mee-slapende wordt **gedurende de nacht niet gestoord** door geluiden of licht boven de 5 lux in de kamer
>   - 3.4. **Regelbare lichtintensiteit** van 5 tot 50 lumen
>   - 3.5. Wordt geleverd met **drie standaardgeluiden** en mogelijkheid tot een **eigen opname**
> - 4\. **Reist mee als vertrouwd element** om verwarring bij PD door wijzigende context te verminderen
>   - 4.1. **Modulair systeem** om aan de eisen van de gebruiker te voldoen
>   - 4.2. Laat **verplaatsing zonder gereedschap** naar een nieuwe context toe
> - 5\. **Maximale consumentenkostprijs van € 150 per module**
> - 6\. Toelaten van **plaatsing en configuratie** door ouderen 75+ 
> - 7\. Bestaat uit **metaal, hout en/of plastic**
>   - 7.1. Komt in **3 esthetische varianten**

## Technische beschrijving

### Samenstelling



- Drie modules, elk met een Arduino Nano 33 IoT en een PIR-sensor en één met een speaker, maken via wifi verbinding met een Raspberry Pi 3.
- Op de Pi is een IoT stack geïnstalleerd. ([instructies](https://github.com/basbaccarne/comon_expo))
- Onderlinge communicaties over PIR- en GYRO-detectie (Arduino) en de _system state_ (Pi) gebeurt via het MQTT-protocol. De _system state_ stuurt de leds en speaker in de modules aan.

### Electronica



Lichtarmatuur (x3)
- [Arduino Nano 33 IoT](https://www.gotron.be/arduino-nano-33-iot-zonder-headers.html)
- [Raspberry Pi 3](https://www.raspberrypi.com/products/raspberry-pi-5/)
- [Led-ring](https://www.otronic.nl/nl/24-bit-rgb-leds-ws2812b-cirkel-rond-neopixel.html?source=googlebase&gad_source=1&gclid=Cj0KCQjwkZm_BhDrARIsAAEbX1GCSt1FU_-lqwhs-2C0fQgxupHfj0l1B38h1cv5iahTJv1isrumIbcaAt71EALw_wcB#gad_source_1)
- [PIR sensor](https://www.gotron.be/pir-motion-sensor.html) (x1)
- [Schakelaar](https://www.gotron.be/componenten/schakelmat/schakelaars/toestel/toestelschakelaar-enkelpolig-on-off-spst-6a-250v-zwart.html)

Luidspreker add-on (x1)
- [MP3-module](https://www.gotron.be/dfplayer-pro-een-mini-mp3-speler-met-128mb-geheugen-onboard.html)
- [Luidspreker](https://www.gotron.be/miniatuurluidspreker-66mm-2w-8ohm.html)
Optioneel:
- [AA batterijhouders](https://www.gotron.be/energie/batterijen/batterijhouder/batterijhouder-voor-1-x-aa-cel-met-draden.html) (x3)
- AA batterijen (x3)
- [Step-up converter](https://www.otronic.nl/nl/mt3608-2a-max-dc-dc-step-up-power-module-booster-p.html)

Circuit (kabels, connectoren, weerstanden, etc.)

### Hardware



- Behuizing (x3)
  - [Haak](cad/haak.stl)
  - [Ring](cad/ring.stl)
  - [Pasvorm 1](cad/pasvorm%201.stl)
  - [Pasvorm 2](cad/pasvorm%202.stl)
- Diffuser (x3)
  - [Schijf](cad/schijf.stl)

### Software



- Arduino code voor timing en communicatie (licht en geluid)
  - [Main]("src/pilot/src/main.cpp")
  - [Actuatoren]("src/pilot/src/actuators.cpp")
- Raspberry pi code voor state switching
  - NodeRED [json export]("src/pilot/src/Raspberry Pi/orion_NodeRED.json")
  - Grafana dashboard [json export]("src/pilot/src/Raspberry Pi/orion_Grafana.json")
- Applicatie voor configuratie
<br clear="all">

## Kritische reflectie

De _technological divide_ en de _status quo bias_ blijven een barrière, zowel voor diepgaand gebruikersonderzoek als de uiteindelijke acceptatie. Vooral professionele zorgverleners en daarnaast ook mantelzorgers zien potentieel in het product, wat aangeeft dat Orion op de goede weg is.

Het product ondersteunt momenteel een aantal specifieke situaties. Echter, er zijn nog diverse randgevallen die onderzocht moeten worden om de werking robuuster en breder toepasbaar te maken. De introductie van kunstmatige intelligentie om nachtelijke patronen te analyseren, vormt hierbij een mogelijke benadering.

Hoewel het gebruik bij kinderen enkele inzichten heeft opgeleverd, is het bij nader inzien niet nodig om deze doelgroep verder te behandelen. Het aanpassen van de vormgeving en het instelbaar maken van bepaalde - potentieel stigmatiserende - functies kunnen de adaptatiegraad verhogen. De intuïtieve werking voorkomt een leercurve, waardoor een vroege introductie geen noodzaak is.

## Bijlagen

### Discover
- Literature review
  - [Protocol](https://ugentbe-my.sharepoint.com/:b:/g/personal/elias_verdegem_ugent_be/EdiS3hkiKK1MplGdmVTWungBmxVn0FbBp6aX2gbiq4Yjcw?e=3pP9zS)
  - [Rapport](https://ugentbe-my.sharepoint.com/:b:/g/personal/elias_verdegem_ugent_be/EVpkX9X-c-hKqZcMqP5W1E4BfmoQJAslg8WdfgcqIlADtQ?e=OeRcE2)
- User interviews
  - [Protocol](https://ugentbe-my.sharepoint.com/:b:/g/personal/elias_verdegem_ugent_be/EcmzMGjfi_pDri7_CiFLg6sBVcVGTVBcUN_csnUy3V1scA?e=q4lqXB)
  - [Rapport](https://ugentbe-my.sharepoint.com/:b:/g/personal/elias_verdegem_ugent_be/EUxWuQ6OHRBBsqC9CrPRgI8ByjO5FftoaaS89HSN1k0SQQ?e=l8HrYT)
- Ethnography
  - [Protocol](https://ugentbe-my.sharepoint.com/:b:/g/personal/elias_verdegem_ugent_be/EbZtCITc4uJAq0ycfyGaPi8BeBhuUqo_bVPuqhUFXoU3WQ?e=zYbrPR)
  - [Rapport](https://ugentbe-my.sharepoint.com/:b:/g/personal/elias_verdegem_ugent_be/EUZXoSR17MNIq53AvzIOdvEBZ89_BWPycliHvZ6ZHHcRLg?e=TfPVYO)

### Define
- [Testimonials](https://ugentbe-my.sharepoint.com/:b:/g/personal/elias_verdegem_ugent_be/EWyvy-P7P6lCo79PSqwTZOcBr3zRq12eMHFV4EmILDvBsg?e=ta0Xfr)
- [Literature review](https://ugentbe-my.sharepoint.com/:b:/g/personal/elias_verdegem_ugent_be/EVuqMEwuGKBKsmLIZl0oRTYBc0NNRPol8vBCxzsqA2-cCg?e=Nf0qWs)
- Prototypes wave 1
  - [Protocol](https://ugentbe-my.sharepoint.com/:b:/g/personal/elias_verdegem_ugent_be/EUDGs_sZqw1Cu-SNZ_Z4MUYB4EUygZoMUpzzzmrSuLFlzA?e=GaHmqu) - [enquête](https://ugentbe-my.sharepoint.com/:b:/g/personal/elias_verdegem_ugent_be/Ef0tJbKGW_dAtwJForc6fqsBGBC1jhmTAPsUzSV54qDXcQ?e=y3iexh)
  - [Rapport](https://ugentbe-my.sharepoint.com/:b:/g/personal/elias_verdegem_ugent_be/EYPAxhtVcARDhyRcBSE5QyAB_7105NtN1UUdGcgKd0noVQ?e=lRj64M) - [resultaten enquête](https://ugentbe-my.sharepoint.com/:b:/g/personal/elias_verdegem_ugent_be/ETZRhIU3ZTpDvh90dmZtsAcBM5H1ob_vPhDzmzgHq2v9hA?e=dr1w6v)
- [Matrix evaluation](https://ugentbe-my.sharepoint.com/:b:/g/personal/elias_verdegem_ugent_be/EXnrC_QwjRpIjKC0r4nMURQBxLFSH6Xwk91S0IcJtIyq2Q?e=Yyvibq)
- Prototypes wave 2
  - [Literature review](https://ugentbe-my.sharepoint.com/:b:/g/personal/elias_verdegem_ugent_be/EVuqMEwuGKBKsmLIZl0oRTYBc0NNRPol8vBCxzsqA2-cCg?e=P4wvQc)
  - [Protocol](https://ugentbe-my.sharepoint.com/:b:/g/personal/elias_verdegem_ugent_be/EVgxVO37P6NCvh-ebd2gSRIBjbLRaMpq6a8uFbEiW7BVhg?e=qOb3VR)
  - [Rapport](https://ugentbe-my.sharepoint.com/:b:/g/personal/elias_verdegem_ugent_be/EXnrC_QwjRpIjKC0r4nMURQBxLFSH6Xwk91S0IcJtIyq2Q?e=Yyvibq)
  - [Arduino code Beacon](/tests/Beacon.ino)
  - [Arduino code Breadcrumb](tests/Breadcrumb.ino)
- [User Flow](https://ugentbe-my.sharepoint.com/:b:/g/personal/elias_verdegem_ugent_be/EUmTUIAKd8ZKhQMbT16yuzMBDt6p4VjeiizfwWYc89rwLw?e=mRQy1Y)

### Develop
- Prototypes wave 3
  - [Protocol](https://ugentbe-my.sharepoint.com/:b:/g/personal/elias_verdegem_ugent_be/EQc9bVL98C1Bg9wy_j9wrJwBJp-GJjBEg8ULPVaeS8YLjg?e=RuK1Z6) - [BERT-enquête](https://ugentbe-my.sharepoint.com/:b:/g/personal/elias_verdegem_ugent_be/Ef-kFxQShQdNrK5ER4mzfosBrSAzOw-ppaQV2JV5mDE-QA?e=NEIaNG)
  - [Rapport](https://ugentbe-my.sharepoint.com/:b:/g/personal/elias_verdegem_ugent_be/EZvJdp2McdxAnRVUZE21PdMB0frdUHorjLVcXtSo-ZZe9w?e=HnJsfv)
- Prototypes wave 4
  - [Protocol](https://ugentbe-my.sharepoint.com/:b:/g/personal/elias_verdegem_ugent_be/EbpEEQu65s1MsOD6PxRYUmsBMa9nkP9GNjpH73FM9u82Bg?e=3dqR0F) - [Testing WebUI](https://eaverdeg.github.io/)
  - [Rapport](https://ugentbe-my.sharepoint.com/:b:/g/personal/elias_verdegem_ugent_be/EaTvNlM5hxRDjElFE4yJdeABiT8zmxKg7SMp7_JgvvWh1Q?e=RHhe7Z)
- Prototypes wave 5
  - [Protocol](https://ugentbe-my.sharepoint.com/:b:/g/personal/elias_verdegem_ugent_be/Eba2SJnz_qJLk0D3Vfa5ZnQBhl0F5f7rrHB8iqlQefb_Kw?e=W9rya8)
  - [Rapport](https://ugentbe-my.sharepoint.com/:b:/g/personal/elias_verdegem_ugent_be/EYsSF-ocI9BGpibg7Vrg9c0BDqhcAzFuGdlTmi8KfnNLWw?e=21pjaG)

### Deliver
- [Explainer video]()
  - [Script](https://ugentbe-my.sharepoint.com/:b:/g/personal/elias_verdegem_ugent_be/EcioSIA9y9ZAlRPYxw0DY-EBSUCkpOe41N7b1oHjZXvO0w?e=Y3X2C9)

[^1]: Vriens, K., Sage, C., d’Otreppe, P., Koster, F., & Christiaens, E. (2024, december). _A new era in Belgian healthcare: Key findings and collaborative insights towards implementation of value-based healthcare_. PwC Enterprise Advisory BV. In opdracht van de Belgian Association of Hospital Managers.

[^2]: Alzheimer Liga Vlaanderen. (2020). _Prevalentie van dementie_. Dementie.be. https://www.dementie.be/home/wat-is-dementie/prevalentie/

[^3]: Thomas, T., & Ritter, A. (2022, juni). _Wandering & sundowning in dementia_. Practical Neurology, 21(3), 36–39, 44.

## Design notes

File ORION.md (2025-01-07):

# Projecttitel -Hulpmiddel voor mantelzorgers van personen met dementie -Orion-
*Een smart-home device om slaap en gemoedsrust van de manterlzorger te garanderen door zelfstandigheid van personen met dementie te verhogen * 

*Projectteam: Elias Verdegem; Viktor Fabry*

06/01/2025

## Samenvatting  

Elke vier seconden krijgt iemand wereldwijd de diagnose dementie, wat de druk op mantelzorgers en de zorgsector vergroot. Dit project richt zich op het probleem van verstoorde dag-nachtritmes bij mensen met dementie, wat zowel hun slaap als de nachtrust van hun verzorgers verstoort.

Uit onderzoek, interviews en prototype testen bleek de behoefte aan hulpmiddelen die nachtelijke onrust verminderen en mantelzorgers ondersteunen. De oplossing bestaat uit twee prototypes: de Breadcrumb, een serie lichtjes die een pad vormen om oriëntatie te bieden, en de Beacon, een multi-sensoriele lamp die rust en veiligheid creëert.

Deze prototypes zijn ontworpen om de zelfstandigheid van mensen met dementie ’s nachts te bevorderen, onrust te verminderen en de belasting voor mantelzorgers te verlichten. Zo kunnen mantelzorgers langer zorg bieden zonder in te boeten op hun eigen nachtrust.

Dit project toont de kracht van technologie om de zorg thuis duurzamer en aangenamer te maken voor zowel mensen met dementie als hun verzorgers.
![image](https://github.com/user-attachments/assets/1bc277f8-803a-4f7f-b774-983aeba85a83
![image](https://github.com/user-attachments/assets/ff86eb54-93d0-483a-b74e-2c397e394a67

## Introductie
Max 300 woorden.
Kader je project. Introduceer het probleem en jouw doelstellingen (inclusief boundary conditions).
Maak gebruik van bronverwijzingen ([zie APA stijl](https://www.scribbr.nl/category/apa-stijl/)).

Elke vier seconden krijgt iemand de diagnose van dementie, en met de opkomst van deze ziekte en de crisis in de zorg, worden mantelzorgers fundamenteel om personen met dementie te ondersteunen. Dementie is een wereldwijd probleem dat 55 miljoen mensen treft en jaarlijks 10 miljoen nieuwe gevallen kent. In België lijden ongeveer 200.000 personen aan een vorm van dementie, en door de vergrijzing wordt verwacht dat dit aantal tegen 2070 zal verdubbelen.
Personen met dementie hebben moeite met een standaard slaappatroon, wat leidt tot nachtelijke onrust en dwalen. Dit verstoort niet alleen de nachtrust van de persoon met dementie zelf, maar ook die van hun mantelzorgers, vaak de partner. Deze aanhoudende belasting kan leiden tot fysieke en emotionele uitputting van de mantelzorger, wat de beslissing tot een vaste opname in een woonzorgcentrum kan bespoedigen.
Het doel van dit project is om een oplossing te ontwikkelen die de nachtrust van personen met dementie en hun mantelzorgers bevordert, zodat thuiszorg langer mogelijk blijft. Daarbij is het cruciaal om de autonomie van de zorgbehoevende te ondersteunen en de druk op mantelzorgers te verlagen. Dit vereist oplossingen die rekening houden met de uiteenlopende en veranderende cognitieve en zintuiglijke capaciteiten van personen met dementie. De focus ligt op het minimaliseren van nachtelijke interventies en het ondersteunen van een zelfstandig dag-nachtritme. De ontwikkelde oplossing moet bovendien flexibel zijn en ook in een woonzorgcentrum gebruikt kunnen worden om de professionele zorgverleners te ontlasten

## Methodologie
Max 400 woorden. Beschrijf je methodologie (enkel SEM1, zie les methodologie). Maak hierbij gebruik van een afbeelding om je tijdlijn weer te geven. Op deze tijdlijn moeten minimaal een tijdsincatie te zien zijn, moeten fasen te zien zijn en moeten activiteiten te zien zijn.


Het onderzoek is opgedeeld in twee fasen: de discovery fase en de definitie fase. De discovery fase omvatte een literatuurstudie om een breed en helder beeld te krijgen van dementie, de sociale context en de bestaande oplossingen. Daarnaast werden er etnografische observaties in een dagcentrum uitgevoerd om de problematiek in de praktijk te observeren. In deze fase werden ook interviews afgenomen met mantelzorgers en zorgprofessionals om hun ervaringen en noden te begrijpen. De definitiefase richt zich op het prototypen en testen van oplossingen. Deze fase bestaat uit minimaal twee iteraties waarin verschillende prototypes ontwikkeld, getest en geëvalueerd worden om de meest effectieve oplossing te vinden. Hierbij wordt het 'Think Aloud Protocol' gehanteerd. De nadruk ligt op concept testing en in mindere mate usability testing.

## Discovery
Max. 1000 woorden
### Doestellingen
Wat wilde je bereiken?

-  Een begrip krijgen van wat de ziekte inhoud.
-  Een diepgaand begrip krijgen van de problematiek rond dementie en de impact op mantelzorgers.
-  Het identificeren van de belangrijkste noden en behoeften van mantelzorgers en personen met dementie.
-  Hoe de personen met dementie en mantelzorger dagopvang ervaren.
-  Het in kaart brengen van bestaande technologieën en oplossingen, en het identificeren van onderbelichte thema’s.
  
### Materiaal & methoden
Hoe onderzocht je dit? Wees volledig.
Een antwoord op de vorige vragen werd verkregen via een 
1:  literatuurstudie, hierin gefocust op een onderbouwd begrip vormen van de ziekte, de problematieken die ermee gepaard gaan, de effecten op de
    persoon met dementie en zijn omgeving en de bestaande technologieën die hierin hulp trachten te bieden. Dit aan de hand van analyse van wetenschappelijke artikelen, rapporten en andere relevante documenten       over dementie, mantelzorg en technologische hulpmiddelen.
2:  Ethnografisch onderzoek, dit in de vorm van A Day in the Life. We trachten de positieve en negatieve effecten van dagopvang in kaart te brengen en de doelgroep van dichtbij te observeren om ons begrip van de     ziekte scherper te stellen. Dit waren observaties, field notes en contextual inquiries binnen een dagcentrum.
3:  Groepsgesprekken, dit waren semigestructureerde groepsgesprekken met mantelzorgers en dagverzorgingsmedewerkers in twee woonzorgcentra om ervaringen. Deze groepen werden gebruikt om behoeften, noden,             ideëen en meningen over het project te verkrijgen.

### Resultaten
Literatuurstudie: 
Dementie is een complexe ziekte met uiteenlopende symptomen, dewelke uiteenlopende lasten met zich
meebrengen voor zowel de persoon zelf, als de (informele) zorgverleners. Er is veel onderzoek en innovatie
gaande en vernieuwingen spitsen zich toe op uiteenlopende problematieken.
-  Communicatie en sociale interactie
-  Fysieke veiligheid en bewegingsvrijheid
-  Cognitieve stimulatie en geheugenondersteuning
-  Ondersteuning voor dagelijkse zorgactiviteiten en zelfredzaamheid
Hoewel de meeste technologieën zijn gericht op de patiënt, zijn er weinig toepassingen specifiek gericht op de
emotionele ondersteuning en stressreductie voor mantelzorgers zelf.
Artificiële intelligentie is een belangrijke trend die hierin nieuwe mogelijkheden biedt. Omwille van de leeftijd en
de achteruitgaande cognitieve capaciteiten van het doelpubliek brengt de introductie van nieuwe
technologieën enkele belangrijke complexiteiten met zich mee.

Ethnography: Mantelzorgers zijn zwaar, slechts periodiek onderbroken, belast door de zorg voor personen met dementie.
Dagcentra of een uitstap met een vrijwilliger of 2de lijn mantelzorger bieden een moment van decompressie.
Ze zijn een in de tijd afgebakende oplossing voor mensen in een vroeg stadium van dementie. Een oplossing
die ook in de overige uren van de dag de autonomie van de zorgbehoevende ondersteunt en tegelijkertijd de
druk op mantelzorgers verlaagt, zou de mentale en fysieke last kunnen verlichten en mogelijk de kwaliteit van
leven voor beide partijen verbeteren. De aard en de progressie van dementie heeft een grote invloed op de
benodigde zorg en ondersteuning alsook de fysieke en cognitieve capaciteiten van de zorgbehoevende.
Hieronder nog een fishbone diagram met de belangrijkste zaken m.b.t de belasting van mantelzorgers.


Gebruiksinterviews: Pwd hebben vaak last met een standaard slaappatroon, ze worden ‘s nachts wakker, gedesoriënteerd en beginnen te 
dwalen. Als de persoon met dementie naar het toilet moet is het vaak aangewezen zo min mogelijk extra prikkels te 
hebben, en als er prikkels zijn deze hen te sturen naar, of van het toilet. Zo kan dwalen beperkt worden. Vaak worden de 
MZs dan ook wakker, dit wederzijds om de PwD te helpen, maar ook voor hun eigen gemoedstrust. Er werd vermeld dat 
zowel de MZ als PwD pas gerust zijn wanneer deze weten dat de PwD terug in bed ligt. Vaak wanneer de nachten té zwaar 
worden gaan MZs vaste opname gaan overwegen. Deze beslissing valt hen vaak zwaar. Dat zien ze in het woonzorgcentrum 
ook. De angst voor een nieuwe woonomgeving van de PwD geeft angst voor een versnellende ziekte. Maar een MZ zonder 
slaap gaat er hoe dan ook aan onderdoor.
"Een verstoorde nachtrust van personen met dementie is vaak het duwtje van dagopvang naar vaste opvang." -Joris Cappon

### Conclusies & implicaties
Definieer de belangrijkste designbeslissingen
De belangrijkste designbeslissingen die we kregen waren dat het echt de zelfstandigheid van de pwd moet garanderen. De drempel voor gebruik moet ook laag blijven, het moet zo intuitief mogelijk gebruikt kunnen worden. Optie om de mantelzorger te alarmeren indien nodig moet ook zeker geimplementeerd worden, dit zal zorgen voor meer vertrouwen in het product van de mantelzorger zelf. Vaak zijn huidige producten duur in aankoop of lastig in gebruik, dit moet ook geprobeert worden te doorbreken. De ziekte is voor iedereen anders, en evolueert ook met de tijd. Een op maat oplossing voor elke persoon is noodzakelijk. Het doel is om de nachtrust van de mantelzorger ook weldegelijk prioriteit, het mag niet het geval zijn dat het product de mantelzorger zou wekken. Als de persoon met dementie buiten de kamer is, is het ook noodzakelijk dat het product dit meedeelt aan de mantelzorger, als deze wakker komt.

## Definition
Max. 1000 woorden
### Doestellingen
Wat wilde je bereiken?

-  Het ontwikkelen van concrete prototypes (Breadcrumb en Beacon) die de geïdentificeerde problemen adresseren.
-  Het testen en evalueren van deze prototypes in realistische scenario's.
-  Het verzamelen van feedback van gebruikers en stakeholders om de prototypes te verbeteren

### Materiaal & methoden
Hoe onderzocht je dit? Wees volledig.

-  Prototype ontwikkeling: Ontwikkeling van de Breadcrumb (lichtjes die een pad vormen) en de Beacon (een multi-sensorieel kussen/lamp) gericht op het verbeteren van de nachtrust en zelfstandige nachtelijke oriëntatie.
-  Testprotocollen: Opstellen van testprotocollen om de prototypes systematisch te evalueren met focus op concept testing.
-  Gebruikerstesten: Uitvoeren van gebruikerstesten met mantelzorgers en zorgprofessionals, waarbij de prototypes in realistische scenario's worden uitgeprobeerd. Er wordt gelet op zowel verbaal als non-verbaal gedrag (grime) bij het gebruik van de prototypes.

### Resultaten
Rapporteer over de resultaten (incl. foto's, quotes, analyseframeworks, ...)
### Conclusies & implicaties
Definieer de belangrijkste designbeslissingen

-  De Breadcrumb (lichtjes doorheen het huis, gelinkt aan RFID) werd positief ontvangen door mantelzorgers, omdat het een veilige manier biedt om de PwD terug naar de kamer te leiden.
-  De Beacon biedt multi-sensorische prikkels (licht, geluid) die kunnen helpen bij het reguleren van het dag-nachtritme, en kan gepersonaliseerd worden in functie van de behoeftes.
-  Het product moet interventiearm werken en makkelijk te integreren zijn in een thuisomgeving.
-  Een lange batterijduur of aansluiting op het net is een vereiste.
-  De functionaliteiten van de prototypes moeten worden afgestemd op de context (thuiszorg vs. woonzorgcentrum).
-  De doelgroep bestaat (hoofdzakelijk) uit ouderen wiens mentaal model van gelijkaardige producten beperkt is, waardoor de interactie intuïtief moet zijn.

| ID | Design Requirement | MoSCoW | Source | Date |
| - | - | - | - | - |
| **1** | **ONTLAST DE NABIJE ZORGVERLENERS** | M | User interview | 13/10/2024 |
| **1.1** | **Ontlast de mantelzorger (MZ) door minder verstoorde nachtrust**<br>en biedt geruststelling ook wanneer de DP niet in de onmiddellijke nabijheid is | M | User interview | 13/10/2024 |
| 1.1.1 | Geeft feedback voor de MZ, IZ, PZ over hoe lang (indien te lang) de PD wegblijft | S | Expert review | 13/12/2024 |
| 1.1.2 | Detectie van route en bijhorende tijdsindicatie van de PD | M | Expert review | 13/12/2024 |
| 1.1.3 | De detectie is failsafe en werkt wanneer deuren worden opengelaten | S | Cognitive walkthrough | 25/11/2024 |
| 1.1.4 | Communiceert met een smartphone app (inwonende) MZ & familie | S | Expert review | 13/12/2024 |
| 1.1.5 | Waarschuwingsgevoelidheid is instelbaar | S | Expert review | 13/12/2024 |
| **1.2** | **Ontlast de professionele zorgverlener (PZ) door minder verstoorde nachtshift** | S | Ethnography | 15/10/2024 |
| 1.2.1 | Personaliseerbare spraakberichten minimaliseren interventies door PZ | S | Expert review | 13/12/2024 |
| 1.2.2 | Communiceert met DECT | C | Expert review | 13/12/2024 |
| 1.2.3 | Waarschuwingsgevoeligheid is instelbaar | M | Expert review | 13/12/2024 |
| **2** | **EMPOWERT EEN BREED SPECTRUM AAN PERONEN MET DEMENTIE (PD)** | M | Literature review | 20/11/2024 |
| **2.1** | **Geeft PD meer zelfstandigheid en eigenwaarde en biedt een cognitieve en geruststellende ondersteuning** | M | Think aloud | 13/12/2024 |
| 2.1.1 | Begeleid de PD bij een nachtelijk toiletbezoek | M | User interview | 13/10/2024 |
| 2.1.2 | Oriënteert de PD in de tijd (dag-nacht-onderscheid) | S | User interview | 13/10/2024 |
| 2.1.3 | Beperkt de PD niet in zijn (bewegings)vrijheid | M | Ethnography | 15/10/2024 |
| 2.1.4 | Respecteert de privacy van de DP en de MZ | M | State of the Art | 16/12/2024 |
| 2.1.5 | De interacties zijn intiütief | M | Think aloud | 13/12/2024 |
| **2.2** | **Biedt een meerwaarde voor >50% van de varianten en gradaties van de ziekte** | M | Literature review | 12/10/2024 |
| 2.2.1 | [...] verstoorde oriëntatie in tijd | M | Literature review | 12/10/2024 |
| 2.2.2 | [...] verstoorde oriëntatie in ruimte | C | Literature review | 12/10/2024 |
| 2.2.3 | [...] doolgedrag | S | Literature review | 12/10/2024 |
| **2.3** | **Bevordert het circadiaans ritme van de PD** | C | Literature review | 20/11/2024 |
| 2.3.1 | Bevat enkel functies waarvan de doeltreffendheid in de praktijk werd aangetoond | M | Expert review | 13/12/2024 |
| 2.3.2 | Multisenoriële snoezelfuncties bevorderen het inslapen | S | Expert review | 13/12/2024 |
| 3.1.3 | Dringt geen onnodige of ongewenste functies op | M | Think aloud | 13/12/2024 |
| 2.3.4 | Snoezelfuncties en kloksturing zijn personaliseerbaar door de MZ | M | Think aloud | 13/12/2024 |
| 2.3.4.1 | PD wordt actief betrokken bij de configuratie van het toestel | C | Think aloud | 13/12/2024 |
| **2.4** | **Evolueert mee met de PD** | M | Ethnography | 15/10/2024 |
| 2.4.1 | Reist mee met de PD doorheen het verloop van de ziekte als vertrouwelijk element | S | Ethnography | 15/10/2024 |
| 2.4.2 | Kan eenvoudig geïnstalleerd worden ongeacht de omgeving | M | Think aloud | 13/12/2024 |
| **3** | **VOORKOMT BIJKOMENDE EMOTIONELE, COGNITIEVE OF FYSIEKE BELASTING** | M | Think aloud | 13/12/2024 |
| **3.1** | **Voorkomt agitatie en verwarring van de PD** | M | Think aloud | 13/12/2024 |
| 3.1.1 | Veroorzaak geen gevoel van schaamte of confrontatie | M | Think aloud | 13/12/2024 |
| 3.1.2 | Doet de omgeving vertrouwelijk, herkenbaar en veilig aanvoelen voor de PD | S | Think aloud | 12/12/2024 |
| 3.1.3 | Trekt enkel de aandacht van de PD wanneer functioneel relevant | M | Think aloud | 13/12/2024 |
| 3.1.4 | Kan om met foutieve interacties en heeft een beveiligde bediening waar nodig | M | Expert review | 13/12/2024 |
| 3.1.5 | Belichting veroorzaakt geen verblinding of agitatie | M | Think aloud | 13/12/2024 |
| 3.1.6 | Prikkelintensiteit is afgesteld op het beoogde doel en is contextueel | M | Think aloud | 13/12/2024 |
| **3.2** | **Voorkomt bijkomende belasting van de zorgverlener(s)** | M | Cognitive walkthrough | 25/11/2024 |
| 3.2.1 | Vermijdt prikkels die de nachtrust van de meeslapende verstoren | M | Cognitive walkthrough | 25/11/2024 |
| 3.2.2 | Heeft een batterijlevensduur van minimaal 1 jaar of is aansluiting op netstroom | M | Cognitive walkthrough | 13/12/2024 |
| **4** | **OPTIMALISEERT HET ADOPTIEPOTENTIEEL** | M | Think aloud | 13/12/2024 |
| 4.1 | Kost minder dan €800 | M | State of the Art | 16/12/2024 |
| 4.2 | Een IZ (MZ of familie) kan het product zelf installeren en configureren via een app | S | Cognitive walkthrough | 25/11/2024 |
| 4.3 | Functies worden gradueel geïntroduceerd op tempo van de gebruiker | S | Think aloud | 13/12/2024 |
| 4.4 | Heeft een emotionele en of nostalgische waarde voor de gebruiker(s) | C | Think aloud | 13/12/2024 |
| **5** | **NOT HAVES / NICE TO HAVES** | | | |
| 5.1 | Koppeling met wearable (hartslagsensor) | C | State of the Art | 16/12/2024 |
| 5.2 | Koppeling met geavanceerde detectiesystemen (Mintt) | C | State of the Art | 16/12/2024 |
| 5.3 | Activiteit monitoring | C | State of the Art | 16/12/2024 |
| 5.4 | Meeneembaar op verplaatsing | C | User interview | 13/10/2024 |

## Bill of materials
#### Breadcrumb (x2)
- Processor (Arduino)
- Aan/uit-klop
- Zigbee zender en ontvanger
- Acceleratiemeter
- RGB LEDs
- Voeding (5V) & circuits
- Behuizingscomponenten (te ontwerpen)
#### Beacon (x1)
- Processoren (Arduino)
- Aan/uit-knop
- Zigbee zender en ontvanger
- IR-camera module (AMG8833)
- Klokmodule (RTC)
- Lichtsensor
- Ultrasone aroma verstuiver (x2)
- RGB LEDs (x2)
- Luidspreker (versterker, MP3-module, Micro-SD geheugenkaart)
- Voeding (5V) & circuits
- behuizingscomponenten (te ontwerpen)
#### Overige
- Code voor sturing timing & communicatie
- App voor instellen & personaliseren
- Biosensors voor product evaluation testing

## Kritische reflectie
Max. 500 woorden

## Bronnen
Voeg je volledige bibliografie toe van bronnen naarwaar je verwees.

## Bijlagen

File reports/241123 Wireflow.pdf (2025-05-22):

I

I

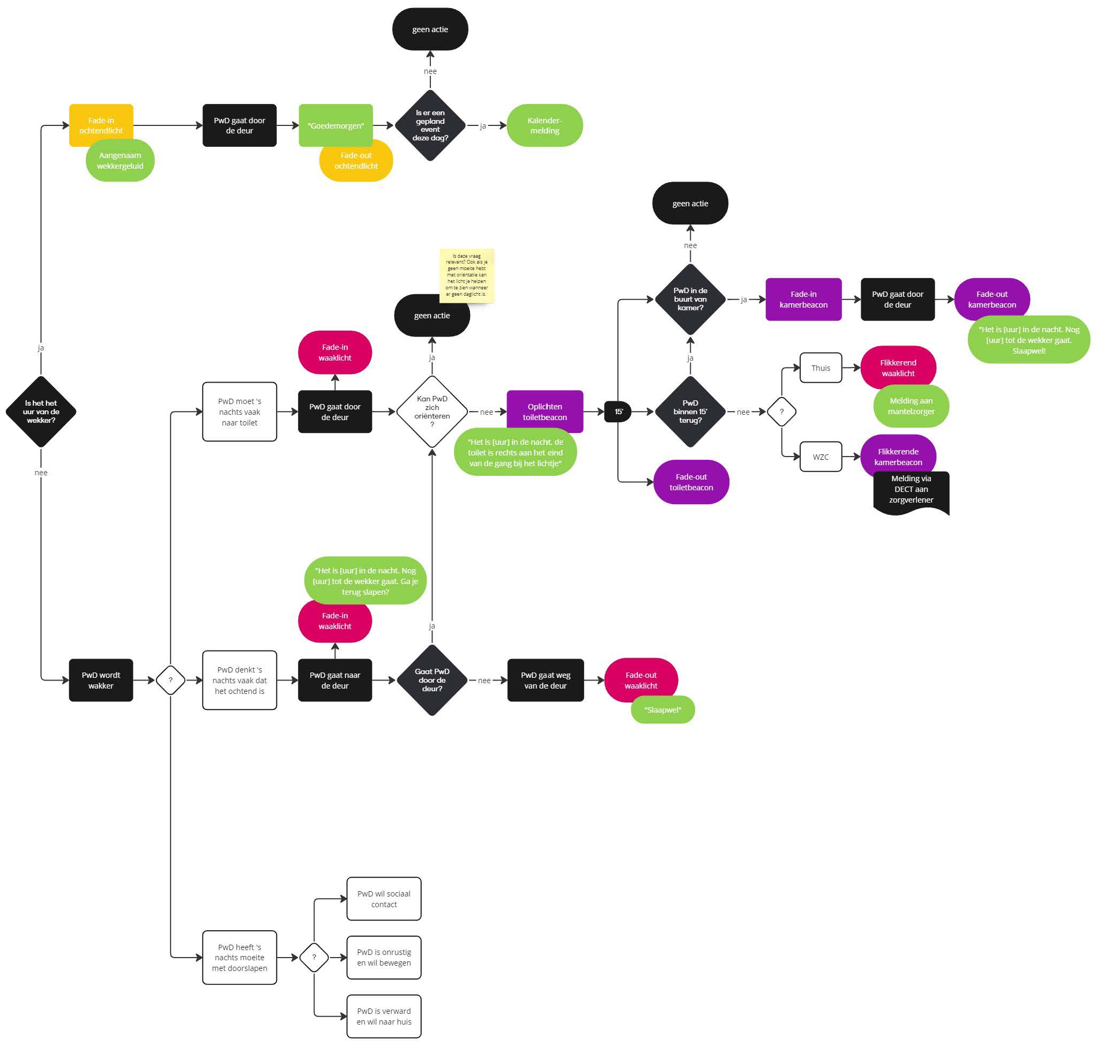
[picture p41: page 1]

nee

PwDmoet 's
nachts vaak
naar toi let

PwD denkt 's
nachts vaak dat
het ochtend is

PwD heeft 's
nachts moeite
met doorslapen

~

PwD wil sociaal
contact

PwD is onrustig
en wil bewegen

PwD is verward
en wil naar huis

nee

ja
I
- ja ,_.

ls de!e vra=!
Jelevam?Ook' als ~
gHn moe(te hebt
~ :o~ma'lte .k.an
het l':cht je he'pen
om te ~nwanneer
er g.een dagl:cht is.
- nee
torlet is rechts aan het ernd

-nee

nee

- ja
t

ja
I

# -nee 0

Thuis

WZC

Flikkerende
kamerbeacon

Melding via
DECT aan
zorgver1ener

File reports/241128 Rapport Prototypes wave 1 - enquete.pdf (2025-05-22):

# Resultaten enquête prototypes wave 1

10/12/2024
Opgelet: bij vraag 5 worden de waarden omgekeerd
vraag 1 | Is dit product volgens u een meerwaarde voor de persoon met dementie? (meer zelfstandigheid, betere nachtrust, verminderde sundowning, …) | -2 | Helemaal niet
vraag 2 | In welke mate denkt u dat dit product de nachtrust van de mantelzorger zou verbeteren? | -1 | Eerder niet
vraag 3 | Hoe gebruiksvriendelijk vindt u dit product voor zowel de persoon met dementie als de mantelzorger? | 0 | Neutraal
vraag 4 | Hoe waarschijnlijk zou u dit product aanbevelen aan andere mantelzorgers of zorgprofessionals? | 1 | Eerder wel
vraag 5 | Verwacht u zich aan nadelen en risico’s bij het gebruik van dit product? Indien ja, licht toe in het vak vrije feedback. | 2 | Zeker en vast
Klinkklok | Breadcrumb | Vloerlicht
Pseudoniem | Respondent type | Locatie | Datum | 1.1 | 1.2 | 1.3 | 1.4 | 1.5 | 1.TOT | 2.1 | 2.2 | 2.3 | 2.4 | 2.5 | 2.TOT | 3.1 | 3.2 | 3.3 | 3.4 | 3.5 | 3.TOT
Jorick Cappon | Centrumleider | Huize Ter Walle | 25/11/2024 | 2 | 1 | 0 | 1 | -1 | 3 | 2 | 2 | 2 | 1 | 0 | 7 | 2 | 1 | 2 | 1 | 0 | 6
Louis Mestdagh | Orthopedagoog CDV | Huize Ter Walle | 25/11/2024 | 0 | 0 | 1 | 2 | 2 | 5 | 0 | 1 | 1 | 2 | 2 | 6 | 0 | 1 | 1 | 2 | 2 | 6
Virginie Debreyne | Medewerker dagcentrum | Huize Ter Walle | 25/11/2024 | 2 | 2 | 2 | 2 | 2 | 10 | 1 | 1 | 1 | 1 | 1 | 5 | 2 | 1 | 2 | 2 | 2 | 9
Hilde Van Eecke | MZ en partner van Omer Syselinck | Huize Ter Walle | 25/11/2024 | -1 | 1 | 0 | 0 | 0 | 0 | 1 | 0 | 0 | 0 | 0 | 1 | 0 | 1 | 0 | -1 | 0 | 0
Léna De Saedeleer | MZ en partner van Antoine Goemaere | Huize Ter Walle | 25/11/2024 | 1 | 0 | 0 | 2 | 1 | 4 | 0 | -1 | -1 | -1 | 1 | -2 | 0 | 1 | 1 | 2 | 2 | 6
Isabelle Lesage | MZ en dochter van Godelieve Vanpeteghem | Huize Ter Walle | 25/11/2024 | 1 | 0 | 0 | 1 | 2 | 4 | 1 | 1 | 0 | 1 | 2 | 5 | 2 | 1 | 2 | 2 | 2 | 9
Marenella Delabie | MZ voor Michèle Cavelier | Huize Ter Walle | 25/11/2024 | 1 | 0 | 2 | 1 | 1 | 5 | 1 | 2 | 2 | 2 | 2 | 9 | -1 | 0 | 0 | 0 | 1 | 0
Lieve Van Peteghem | Referentiepersoon fixatie en valpreventie en palliatieve werkgroep | Sint-Eligius | 28/11/2024 | 1 | 1 | 1 | 1 | 0 | 4 | 1 | 1 | 1 | 1 | 0 | 4 | -1 | 0 | -1 | -1 | 1 | -2
Anneleen Vervaet | Ergotherapeut | Sint-Eligius | 28/11/2024 | 1 | 0 | 1 | 1 | 0 | 3 | 1 | 1 | 2 | 1 | 0 | 5 | 0 | 1 | 1 | 0 | 0 | 2

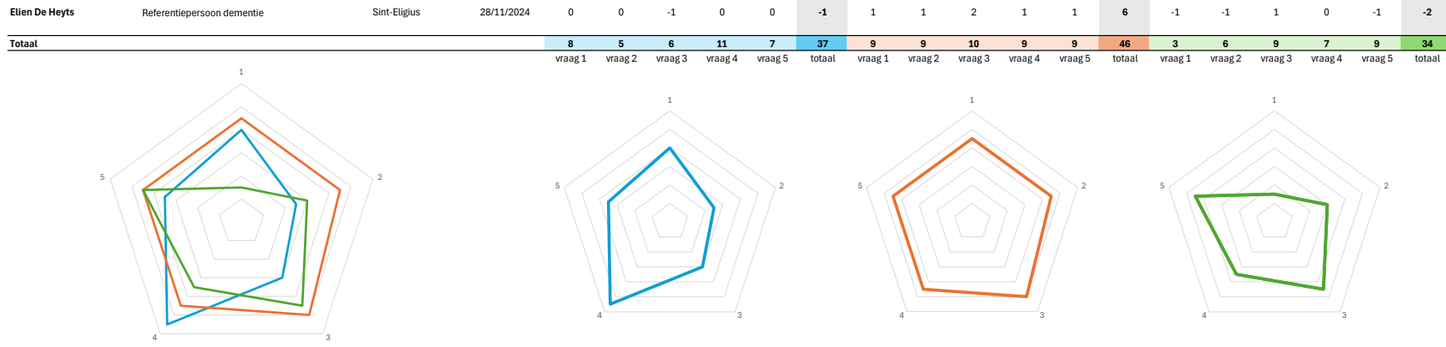
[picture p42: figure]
Elien De Heyts; Referentiepersoon dementie; Sint-Eligius; Totaal; vraag 1; vraag 2; vraag 3; vraag 4; vraag 5; totaal; totaal 1

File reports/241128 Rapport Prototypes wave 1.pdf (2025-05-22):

Gebruiksgericht ontwerpen Viktor Fabry Elias Verdegem 2024 – 2025 | 1
Prototypes wave 1 | Rapport
Hulpmiddel voor mantelzorgers van personen met dementie (werktitel) | 28/11/2024

## Projectinformatie

Project: Een oplossing ter bevordering van de slaap van personen met dementie met een verstoord dag-nacht-ritme en hun mantelzorgers.
Interviewers: Elias Verdegem en Viktor Fabry, studenten industrieel ontwerpen, opdracht gebruiksgericht ontwerpen

Gebruikte afkortingen:
PwD: Persoon met dementie / Person with Dementia
MZ: mantelzorger

## Onderzoeksdoel

Personen met dementie (PwD) hebben moeite met een standaard slaappatroon, ze worden in de nacht wakker en beginnen met hun omgeving te interageren. Sommigen worden onrustig of kleden zich aan en beginnen aan hun dag. De MZs (vaak de partner) moet hierdoor soms meerdere malen per nacht opstaan om de PwD gerust te stellen en terug in bed te krijgen. Deze handelingen zorgen voor een slechte nachtrust voor de MZ. De bedoeling van dit onderzoek is om de last van de MZ te verlagen. In het bijzonder het bevorderen van de nachtrust. Door in gesprek te gaan met medewerkers van woonzorgcentra kunnen we een bredere inzicht krijgen op waar de grens ligt voor MZs om tot vaste opname te gaan. Daarnaast kunnen gesprekken met MZs een inkijk geven in de impact van dit probleem en de verschillende facetten bij het voordoen van dit probleem. Een dagcentrum is een ideale plaats om verschillende visies te verkrijgen over de probleemruimte. Zo kunnen we PwD in verschillende stadia waarnemen, spreken met zorgwerkers, alsook de MZs over hun ervaringen.
We gebruiken onze eerste rudimentaire prototypes als basis van de interactie met de future-users.

## Methodes

Er werden twee groepsgesprekken georganiseerd in twee verschillende woonzorgcentra. De eerste groep bestond voornamelijk uit MZs, terwijl de tweede groep samengesteld was uit zorgmedewerkers van het woonzorgcentrum. Elk gesprek was opgedeeld in twee hoofddelen: een algemeen gesprek waarin wij onze onderzoeksvragen bespraken en een sessie waarin wij onze prototypes voorlegden.
Tijdens het algemene gesprek lag de nadruk op het luisteren naar de antwoorden van de deelnemers. We probeerden zoveel mogelijk input te verzamelen, zowel binnen de thema’s die we al hadden verkend als door nieuwe inzichten te ontdekken die verder onderzoek verdienen.
Voor het prototypegedeelte maakten we gebruik van enquêtes om de antwoorden van alle respondenten gestructureerd en consistent vast te leggen. Dit hielp om groepsinvloeden te minimaliseren, aangezien meningen in een open gesprek gemakkelijk door andere deelnemers beïnvloed kunnen worden.

## Protocol

241122 Protocol Prototypes.pdf (https://ugentbe-my.sharepoint.com/:b:/g/personal/elias_verdegem_ugent_be/EUDGs_sZqw1Cu-SNZ_Z4MUYB4EUygZoMUpzzzmrSuLFlzA?e=A92BTm)
241113 Protocol Prototype wave 1 - enquete.docx (https://ugentbe-my.sharepoint.com/:w:/g/personal/elias_verdegem_ugent_be/EQEY5fC3ztJLkP-Pl2MDtAYBoQ0Pl3sLowA8ZIyqokjB1w?e=VpTBwX)

Gebruiksgericht ontwerpen Viktor Fabry Elias Verdegem 2024 – 2025 | 2

## Steekproefomschrijving

De bevraging ging door op 2 locaties. In WZC Huize Ter Walle in Menen op 25/11/2024 (N = 7) en in WZC Sint-Eligius in Lochristi op 28/11/2024 (N = 3). Het onderzoek duurde telkens ongeveer 1,5 à 2u. Er waren meer respondenten aanwezig bij de bevragingen, maar niet iedereen was in staat of vond het wenselijk om de enquête in te vullen. We lijsten hieronder enkel de personen op waarvan de gegevens via de enquête hebben kunnen verzamelen.
Pseudoniem | Respondent type | Datum | Locatie
Jorick Cappon | Centrumleider | 25/11/2024 | Huize Ter Walle
Louis Mestdagh | Orthopedagoog CDV | 25/11/2024 | Huize Ter Walle
Virginie Debreyne | Medewerker dagcentrum | 25/11/2024 | Huize Ter Walle
Hilde Van Eecke | MZ en partner van Omer Syselinck | 25/11/2024 | Huize Ter Walle
Léna De Saedeleer | MZ en partner van Antoine Goemaere | 25/11/2024 | Huize Ter Walle
Isabelle Lesage | MZ en dochter van Godelieve Vanpeteghem | 25/11/2024 | Huize Ter Walle
Marenella Delabie | MZ voor Michèle Cavelier | 25/11/2024 | Huize Ter Walle
Lieve Van Peteghem | Referentiepersoon fixatie en valpreventie en palliatieve werkgroep | 28/11/2024 | Sint-Eligius
Anneleen Vervaet | Ergotherapeut | 28/11/2024 | Sint-Eligius
Elien De Heyts | Referentiepersoon dementie 28/11/2024 | Sint-Eligius
Roman | Persoon met dementie in het dagcentrum | 28/11/2024 | Sint-Eligius

Gebruiksgericht ontwerpen Viktor Fabry Elias Verdegem 2024 – 2025 | 3

## Gesprekken

### Impact van dementie op het dag-nachtritme

Pwd hebben vaak last met een standaard slaappatroon, ze worden ‘s nachts wakker, gedesoriënteerd en beginnen te dwalen. Als de persoon met dementie naar het toilet moet is het vaak aangewezen zo min mogelijk extra prikkels te hebben, en als er prikkels zijn deze hen te sturen naar, of van het toilet. Zo kan dwalen beperkt worden. Vaak worden de MZs dan ook wakker, dit wederzijds om de PwD te helpen, maar ook voor hun eigen gemoedstrust. Er werd vermeld dat zowel de MZ als PwD pas gerust zijn wanneer deze weten dat de PwD terug in bed ligt. Vaak wanneer de nachten té zwaar worden gaan MZs vaste opname gaan overwegen. Deze beslissing valt hen vaak zwaar. Dat zien ze in het woonzorgcentrum ook. De angst voor een nieuwe woonomgeving van de PwD geeft angst voor een versnellende ziekte. Maar een MZ zonder slaap gaat er hoe dan ook aan onderdoor.
De grootste oorzaken van het opstaan ‘s nachts is wat lastig te pinnen, maar de vermelde redenen zijn:
- Behoefte aan toiletbezoek
- Desoriëntatie en verwardheid
- Honger
- Medische problemen, zoals de effecten van medicatie
In WZC Sint-Eligius worden diverse strategieën ingezet om nachtelijke onrust bij bewoners te verminderen:
- Het laten branden van een lichtje in de toiletruimte.
- Het gebruik van domoticasystemen met sensoren om bewoners te monitoren.
- Het geleidelijk afbouwen van bedhekken, met alternatieven zoals lagere bedden en halve bedsponden. Thuis maken sommige MZs gebruik van camera’s of babyfoons om een persoon met dementie in de gaten te houden. Een zorgprofessional merkt op:
"Observaties worden er wel gedaan. Familieleden plaatsen camera's."
Dit toont aan dat MZs vaak creatieve oplossingen bedenken om de veiligheid van hun naasten te waarborgen.

### Beperkingen van bestaande oplossingen

Geavanceerde domoticasystemen met sensoren zijn vaak te duur of te ingrijpend om te installeren voor thuisgebruik. Het gebruik van verlichting in gangen of slaapkamers kan soms juist verwarring en onrust veroorzaken.

Een zorgprofessional geeft aan:
"Complete duisternis is eigenlijk veel beter."
Dit onderstreept dat verlichting, hoewel in sommige gevallen nuttig, ook negatieve effecten kan hebben.

"Ik denk dat dat vooral de MZ is, hè, die moet ontlast worden, als dat te zwaar begint te worden"
Een citaat van een zorgmedewerker van het woonzorgcentra. Op zich een normale zin, maar het toont het respect en belang voor de MZ. Deze doelgroep heeft een groot belang als het gaat over de zorg in België.

Gebruiksgericht ontwerpen Viktor Fabry Elias Verdegem 2024 – 2025 | 4

## Prototypes

### Klinkklok

Een wederkerige opmerking mbt de klinkklok was dat de lichtgevende klink juist een extra trigger zou zijn om de PwD naar buiten te laten gaan. Wat voor extra verwarring zou zorgen. Het idee waarbij de MZ op een rustige manier kon meekrijgen hoelang de PwD weg was, was dan een van de positieve aspecten. Hoewel de MZs nog steeds niet echt een gevoel van veiligheid erbij kregen. De meesten willen op de hoogte zijn wanneer de PwD uit de kamer is. Alsook zou spraak in de klinkklok zorgen voor verwarring.

### Breadcrumbs

De feedback over de breadcrumbs bij de MZs was over het algemeen positief. Wanneer PwDs nachts de kamer verlaten zijn deze vaak op dool, op zoek naar triggers. Als die triggers dan de breadcrumbs zijn die de PwD terug naar de kamer brengen wordt het beoogde effect bereikt.

### Vloerlicht

De reacties mbt het vloerlicht waren eerder gemengd. De pink noise werd in Huize Ter Walle als storend, ook voor de MZ, ervaren. In Sint Eligius was de feedback positiever. Enkelen geloofden, ook op basis van eigen snoezelexperimenten, in de werking en het rustgevend effect.

### Inzichten met betrekking tot de prototypes

Spraak in de Klinkklok zou tot verwarring kunnen leiden.
De effectiviteit van de verschillende prototypes is sterk afhankelijk van het individu en het stadium van dementie. "Ik denk dat ze dat ook weer heel verwarrdend zullen vinden. Dat is heel individueel hé ja, en ook in een beginfase". Dit citaat illustreert dat er geen “one size fits all” oplossing is.
De timing van de introductie van de nieuwe technologie is cruciaal voor de aanvaarding en effectiviteit ervan. Om die window zo breed mogelijk te maken in het belangrijk om met heel basis zintuigelijke prikkels te werken. Deze kunnen reflexen triggeren, waardoor een leercurve heel beperkt is.

### Inzichten voor het vervolgonderzoek

Interviews met MZs die in de 'inleunflat' wonen kunnen een goede testgroep zijn, aangezien zij zich in een overgangsfase bevinden van thuiszorg naar vaste opname.
Meer informatie verzamelen over hun optische sensoren om de haalbaarheid voor thuisgebruik te bepalen.
Dieper ingaan op de individuele behoeften van personen met dementie en hun MZs om persoonsgerichte oplossingen te ontwikkelen.
Verder onderzoek doen naar de invloed van licht en geluid op nachtelijke onrust, rekening houdend met de bevinding dat complete duisternis soms de voorkeur heeft.

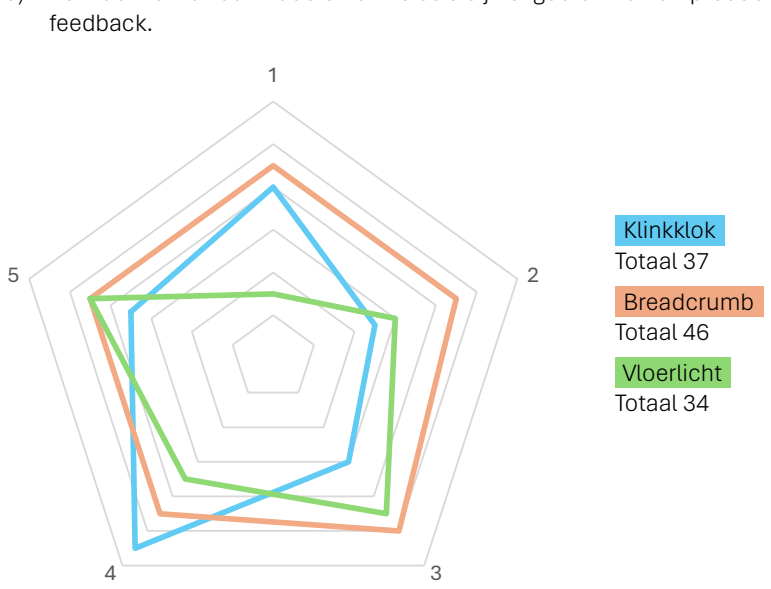
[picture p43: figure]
feedback.; -Klinkklok- Totaal 37 -Breadcrumb- Totaal 46 -Vloerlicht- Totaal 34

Gebruiksgericht ontwerpen Viktor Fabry Elias Verdegem 2024 – 2025 | 5

### Resultaten van de enquête

1) Is dit product volgens u een meerwaarde voor de persoon met dementie? (meer zelfstandigheid, betere nachtrust, verminderde sundowning, …)
2) In welke mate denkt u dat dit product de nachtrust van de mantelzorger zou verbeteren?
3) Hoe gebruiksvriendelijk vindt u dit product voor zowel de persoon met dementie als de mantelzorger?
4) Hoe waarschijnlijk zou u dit product aanbevelen aan andere mantelzorgers of zorgprofessionals?
5) Verwacht u zich aan nadelen en risico’s bij het gebruik van dit product? Indien ja, licht toe in het vak vrije

De breadcrumbs scoren op alle vragen (muv vraag 4) het hoogst. Dergelijke systemen worden zowel in woonzorgcentra als bij thuiszorg geknutseld voorzien. Dit bewijst hun effectiviteit, doch hebben die gebruikte systemen problemen waarop verbeterd kan worden.
Enkel de klinkklok scoort hoger op de vraag of men dit aan anderen zou aanraden. De vermoedelijke reden hiervoor is dat men meerdere malen aangaf dat dit het beste zou werken in een vroeg stadium van de ziekte. Een tijdige introductie is voor een goede werking hiervan dus cruciaal.

Gebruiksgericht ontwerpen Viktor Fabry Elias Verdegem 2024 – 2025 | 6

## Conclusie

De gesprekken met zorgprofessionals en de MZ leverden waardevolle inzichten op in de complexiteit van het probleem van het verstoorde dag-nachtritme bij personen met dementie. De ervaringen en observaties van de respondenten benadrukken de noodzaak om rekening te houden met individuele verschillen en de specifieke behoeften van zowel de persoon met dementie als de MZ. De aanbevelingen voor vervolgonderzoek bieden aanknopingspunten om de prototypes verder te verfijnen en te komen tot effectieve oplossingen die de nachtrust van alle betrokkenen kunnen bevorderen.

## Implicaties

- Het product mag niet de nachtrust van de MZ verstoren.
- Het product moet een geruststellende invloed hebben op zowel de PwD als de MZ.
- Hiervoor moet het product de zelfstandigheid van de PwD bevorderen op een veilige manier.
- En moet het op een niet opdringerige manier feedback geven.
- Het product maakt eventueel monitoring mogelijk met respect voor de privacy van de PwD en meeslapende.
- Het product moet subtiele prikkels gebruiken die niet overweldigend of verwarrend zijn.
- Het product gebruikt enkel prikkels die aangetoond effectief zijn.
- Het product geeft prikkels die reflexen triggeren.
- Het product wordt in een vroeg stadium geïntroduceerd.
- Het product vermijd complexe spraaksystemen of overmatig gebruik van licht kan verwarring veroorzaken.
- Het product moet aanpasbaar zijn aan verschillende stadia van dementie en individuele behoeften.
- Hardware- of softwarematige modulariteit.
- Fijnmazige aanpasbaarheid o.b.v. persoonlijke voorkeuren is mogelijk.
- Het product moet eenvoudig in een thuisomgeving of woonzorgcentrum geïntegreerd kunnen worden zonder ingrijpende aanpassingen aan de infrastructuur.
- Het product moet interventiearm werken
- Het product heeft een lange batterijduur of is aangesloten op het net.

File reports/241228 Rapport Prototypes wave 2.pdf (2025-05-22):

Gebruiksgericht ontwerpen Viktor Fabry Elias Verdegem 2024 – 2025 | 1
Prototypes wave 2 | Rapport
Hulpmiddel voor mantelzorgers van personen met dementie (werktitel) | 28/12/2024

## Projectinformatie

Project: Een oplossing ter bevordering van de slaap van personen met dementie met een verstoord dag-nacht-ritme en hun mantelzorgers.
Interviewers: Elias Verdegem en Viktor Fabry, studenten industrieel ontwerpen, opdracht gebruiksgericht ontwerpen

Gebruikte afkortingen:
PwD: Persoon met dementie / Person with Dementia
MZ: mantelzorger
PZ: professionele zorgverlener

## Onderzoeksdoel

In de voorgaande test werd duidelijk welke cognitieve hulpmiddelen wenselijk zijn in een de context van thuiszorg en bij uitbreiding in woonzorgcentra voor PwD.
Op basis van een Matrix Evaluation (https://ugentbe-my.sharepoint.com/:b:/g/personal/elias_verdegem_ugent_be/EXnrC_QwjRpIjKC0r4nMURQBxLFSH6Xwk91S0IcJtIyq2Q?e=oUiHGj) trachtten we de vergaarde informatie uit de eerste wave van prototypes enkele online testimonials (https://ugentbe-my.sharepoint.com/:b:/g/personal/elias_verdegem_ugent_be/EWyvy-P7P6lCo79PSqwTZOcBr3zRq12eMHFV4EmILDvBsg?e=fmlzez) en dit artikel over wandering & sundowning (https://ugentbe-my.sharepoint.com/:b:/g/personal/elias_verdegem_ugent_be/EWUfGbboJ3lEpfgbiKusCzUB6GKPMzEx7aGyawt5m2cBug?e=xttseU) (key takeaways) (https://ugentbe-my.sharepoint.com/:b:/g/personal/elias_verdegem_ugent_be/EVuqMEwuGKBKsmLIZl0oRTYBc0NNRPol8vBCxzsqA2-cCg?e=Rsgb1m) te verwerken tot een productconcept dat een antwoord biedt aan de voornaamste noden.
We implementeerden:
- Multi-sensorieel avond-ochtend-ritueel om nachtrustkwaliteit te bevorderen
- Cognitief-zintuigelijke ondersteuning voor zelfstandige nacht-oriëntatie in ruimte met veiligheidsfunctie

We wensen de gewenste functionaliteiten en de user-product-interacties die deze moeten triggeren in kaart te brengen. Alsook wat dit impliceert om de vorm en uitvoering (wijze van montage, etc) van het product.

## Methodes

Wizard of Oz testing van minimal viable product prototypes.
Think aloud en observatie van fysieke en emotionele reacties.
In de kantlijn van deze testen werd van de gelegenheid gebruik gemaak om via contextual inqueries en expert interviews maximale input te vergaren via het aanwezige zorgpersoneel.

## Protocol

241122 Protocol Prototypes wave 1.pdf (https://ugentbe-my.sharepoint.com/:b:/g/personal/elias_verdegem_ugent_be/EUDGs_sZqw1Cu-SNZ_Z4MUYB4EUygZoMUpzzzmrSuLFlzA?e=727RLC)

Gebruiksgericht ontwerpen Viktor Fabry Elias Verdegem 2024 – 2025 | 2

## Steekproefomschrijving (N = 3)

De testen werden elk op een ander tijdstip en op een andere locatie uitgevoerd. In totaal werden 3 testen uitgevoerd. Er werden bevragingen gedaan bij professionele zorgverleners en mantelzorgers. Aangezien deze niet expliciet deel uitmaken van de uitgevoerde test, nemen we ze niet op in het steekproefaantal. Doch worden de bevindingen uit deze gesprekken wel meegenomen in de rapportering.

Pseudoniem | Respondent type | Datum | Locatie
Lieve Van Peteghem | Referentiepersoon fixatie en valpreventie en palliatieve werkgroep | 13/12/2024 – case 1 | Sint-Eligius
Elien De Heyts | Referentiepersoon dementie 13/12/2024 – case 1 | Sint-Eligius
Roger | Testpersoon: MZ van PwD in aanleuflat | 13/12/2024 – case 1 | Sint-Eligius
André Verschaffel | Testpersoon: PwD (gevorderde) | 25/12/2024 – case 2 | Thuis
Leana Haerens | MZ en partner van André | 25/12/2024 – case 2 | Thuis
Andrea Vansteenkiste | Testpersoon: oudere | 29/12/2024 – case 3 | Huize Ter Walle

## Gesprekken vooraf

### Case 1 – Lieve Van Peteghem en Elien De Heyts

Het gesprek vooraf gaat door in de zithoek, zonder het bijzijn van Roger en zijn partner. De prototypes worden getoond en toegelicht vooraf aan het installatie in de context. We doorlopen de hypothetische werking in de scenario’s uit het protocol.

Een spraakfunctie is in enkele gevallen toch wenselijk.
“Het spraakbericht ‘Het is nog nacht’ Dit zou voor veel van de gasten in de vaste afdeling van Sint-Eligius kunnen werken. Nu moet er telkens iemand tot aan de kamer gaan om de persoon uit te leggen dat het nog geen tijd is om op te staan. [Elias: Als ze geen klok kunnen lezen, kunnen ze dan soms nog wel het uur begrijpen?]
“We hebben hier een dame die telkens weer vraagt hoe laat het is, zodat ze zich tijdig kan klaarmaken. Wanneer we haar we haar het uur meegeven, merk je dat ze het begrijp en is ze gerustgesteld. Maar een kwartier later is ze er weer ongerust, met dezelfde vraag.
– Lieve

De waarschuwingsfunctie wordt geapprecieerd, mits voldoende aanpasbaarheid. Te relateren aan gebeurtenissen (verlaten van het bad, verlaten van de kamer, passeren van de badkamerdeur) en instelbaar in vertraging van 5, 10, 15 minuten en context gebonden. In een woonzorgcentrum werkt men met DECT (er worden geen smartphones gebruikt). Bij de mantelzorger zijn smartphones tegenwoordig goed ingeburgerd. Meldingen (en instellingen) zou dus het merendeel van de doelgroep bedienen.
“Vandaag werken we in een aantal kamers met infrarooddetectie van Mintt.”
“De familie kan zelf van thuis uit ziet wat er gebeurt via een online platform.”
“We krijgen dan een melding op onze DECT, maar tegen dat we aan de kamer zijn is de PwD vaak al uit de kamer.” … “Bij valst alarm – een been hangt uit het bed, … – moeten er toch iemand langs gaan om het alarm ter plaatse te resetten.” … “Een geluidsboodschap die de PwD al aanspoort om terug in bed te kruipen, zou een hulp kunnen zijn.”
“Zo een toestel kost €800, voor een camera en een connector in ons noodknopsysteem.”
– Lieve

Lieve vermeld Mintt, Televic, Dasa en Zensi als merken van toestellen die gebruikt worden of in ontwikkeling zijn.

Gebruiksgericht ontwerpen Viktor Fabry Elias Verdegem 2024 – 2025 | 3

### Case 2 – Leana Haerens en André Verschaffel

De voorgesprekken verliepen afzonderlijk. André sliep nog bij aankomst (om 8u).

Leana liet weten dat hij deze week, ten gevolge van de stress die gepaard ging met zijn verjaardagetentje met de familie enkele dagen voordien, al de hele week onrustig was. Hij was die week al 2 keer ’s nachts opgestaan. O.a. vanuit het idee dat hij naar zijn (voormalig) werk (ochtenshift in de bakkerij, opkuis in een feestzaaltje, etc.) moest vertrekken. De dokter n.a.v. deze recente evolutie zijn avonnd-medicatie aangepast.

“Hij vind zijn weg naar zijn bed nog heel goed.”
“Ik moet hem dan geruststellen dat hij het zaaltje niet moet gaan kuisen.” … “Maar ik kan er niet veel tegen zeggen, want dan snauwt hij.”
“Hij heeft geen sleutel meer. Ik zou hem elke nacht kwijt zijn.”
“Ik sta elke dag om 8u op. Als pépé dan nog niet wakker is, ga ik hem wekken om 8u30.” … “Vroeger stond hij om 6u op. Hij zit ’s avonds al om 9u in zijn bed.” … “Al loopt hij ’s avonds vaak te ijsberen in zijn kamer.”
– Leana

Wanneer we André treffen trachten we de voor hem heel verwarrende situatie uit te leggen, zodoende hem gerust te proberen stellen. Het wordt echter snel duidelijk uit de lichamelijke en verbale communicatie dat we hier niet in konden slagen. De materie was duidelijk te confronterend en zorgde voor onrust en kwaadheid. We beslissten om de testen vroegtijdig stop te zetten.

“Wie zegt dat? Ik sta helemaal niet op ’s nachts!”
“Ik heb geen wekker. Ik moet voor niemand ni opstaan.”
– André

Hoewel we het protocol niet hebben kunnen volgen, hebben we wel enkele heel belangrijke lessen meegekregen.
- Bevestiging van het belang van de timing van de introductie van een hulpmiddel in een vroeg stadium.
- Moeilijke acceptatie van vreemde elementen. Cfr. status quo bias.
- Confronterend, in het bijzonder wanneer het product een deelprobleem wenst op te lossen dat bij de persoon in kwestie niet aanwezig is. Maar net zo goed voor deze problemen die er wel zijn. Schaamte is een wezenlijk onderdeel van de ziekte.
- Hoe product zou kunnen worden ‘vermomd’ als een gewoon dagdagelijks toestel (bvb. een nachtlamp, wandlamp) of schijnbaar afwezig zijn, zodat het niet de vinger op de pijnlijke wonde legt. De prikkels moeten voldoende afwezig zijn. Cfr. nudging.
- Een alternatieve strategie zou zijn om het product een emotionele, nostalgische waarde toe te kennen. Het eventueel als een cadeau te geven en de PwD zelf te laten ontdekken hoe het hem zou kunnen helpen. Zonder dat externe ogen er zijn om een (negatief) oordeel te vellen. Hierbij bestaat echter de kans dat het niet zal aanvaard worden.

We merken op dat bij André de geruststelling door een vertrouwd persoon, het helpen herinneren en verhelderen van eventuele verwarring de effectieve oplossing voor het probleem is.
Zijn nachten zijn lang en hij heeft uit zichzelf en met de hulp van Leana een relatief routineus slaappatroon. ’s Avonds in slaap vallen is soms moeilijk, maar het is zonder een verder uitgewerkt prototype moeilijk of een vorm van geluid, geur of snoezellicht hierbij zou kunnen helpen. In de directe omgeving (MZ en familie) lijkt hier weinig vraag naar.
Of het wegnemen van de menselijke factor hierbij nefast is, blijft een essentiële onbeantwoorde vraag.

### Case 3 – Andrea Vansteenkiste

Het voorgesprek vond plaats in de zithoek, zonder aanwezigheid van eventuele mantelzorgers. Andrea benadrukte meteen dat ze niet aan dementie lijdt en gaf aan dat ze daar verre van is, ondanks dat ze soms kleine dingen vergeet. Ze legde uit dat dit soms versterkt wordt door medicatie.

Andrea gaf aan dat ze ondersteuning krijgt bij specifieke taken zoals aankleden en huishoudelijke taken, maar verder nog veel zelfstandig doet. Ze is tevreden met haar daginvulling, waarbij ze dagelijks naar het dagcentrum gaat. Ze eet daar en doet overdag zaken op zelfstandige basis.

Gebruiksgericht ontwerpen Viktor Fabry Elias Verdegem 2024 – 2025 | 4

Op het gebied van slaap beschreef Andrea een vrij stabiel patroon. Ze neemt een inslaappil om 19:00 uur en slaapt meestal binnen een uur in. Andrea wordt zelden ’s nachts wakker, en als dat wel gebeurt (voor een toiletbezoek of wat water), valt ze gemakkelijk weer in slaap. Ze wordt doorgaans rond 7:00 à 8:00 uur wakker. Ze vertelde dat ze weinig hinder ervaart van haar slaapomgeving, al klaagden buren en vrienden soms over nachtelijk geluid door externen. Ze gebruikt een nachtlampje met bewegingsdetectie, wat haar helpt veilig -indien nodig- naar het toilet te gaan.

Tijdens het gesprek gaf Andrea ook aan dat ze vroeger wel eens geslaapwandeld heeft, maar dat dit al jaren niet meer voorkomt. Dit bracht haar op een recente gebeurtenis met een buurvrouw die dementerend is. De buurvrouw had ’s nachts een kwetsuur opgelopen maar wist niet meer hoe dat was gebeurd. Andrea uitte haar bezorgdheid en vroeg zich af of de alarmknop voldoende veiligheid bood, mocht ze zelf ooit nachtelijke problemen krijgen.

Belangrijke punten uit het voorgesprek

- Andrea ziet zichzelf als zelfstandig, met uitzondering van enkele praktische taken zoals aankleden en huishoudelijke hulp.
- Ze is alert op haar geheugenproblemen, maar minimaliseert hun impact op haar dagelijks leven.
- Ze waardeert een veilige en rustige slaapomgeving en is gevoelig voor technische oplossingen die haar autonomie ondersteunen.
- Hoewel ze openstaat voor nieuwe hulpmiddelen, gaf ze aan dat deze niet mogen aanvoelen alsof ze specifiek voor personen met dementie zijn ontworpen, omdat ze dat als confronterend zou ervaren.

## Testen prototypes

### Case 1 – Roger

Deze test gebeurde in het bijzijn van Elien De Heyts als gekende, geruststellende tussenpersoon. Het is licht buiten en de kamer kan slechts zeer beperkt verduisterd worden wat de ecologische validiteit verlaagt. Voor de eerste test zijn de prototypes nog niet met de Wizard Of Oz infrarood bediening uitgerust.
Roger is mantelzorger. Normaalgezien zou de test doorgaan met zijn partner, maar omwille van de gevreesde verwarring die deze verstoring in haar dagritme teweeg zou brengen, verkiest Roger om ze hiervoor niet weg te halen uit de dagopvang. We besluiten om de testen uit te voeren om alvast Roger zijn feedback te verkrijgen.
Het koppel woont in een aanleunflat, waarbij ze elk in een afzonderlijke kamer slapen. Er is een sanitair rechtstreeks gekoppeld aan de kamer van zijn partner die leidt aan de ziekte van dementie.
Roger laat weten dat zijn partner geen probleem heeft met ’s nachts de weg naar het toilet te vinden. We zal ze nadien soms per ongeluk zijn kamer binnenkomen i.p.v. terug in bed te kruipen.
Enkele lessen:
- Plaats de beacon buiten het onmiddellijke bereik van de PwD om afleiding te vermijden.
- De plafondinstallatie is niet in elke context mogelijk.
- De breadcrumb moet ook op schuifdeuren geïnstalleerd kunnen worden.
De testomgeving is erg prikkelrijk, wat de validiteit van de test verlaagt. De geurverstuiving wordt niet opgemerkt.
We leren uit deze test dat het tijdstip van de test zowel voor de duisternis als voor het minimaal verstoren van het dagpatroon van de testpersoon van groot belang is. Een prototype en context die het werkelijke scenario zo dicht mogelijk benaderen is essentieel voor correcte feedback, i.h.b. op vlak van UX.
Bovendien wordt nogmaals bevestigd dat de problematieken erg individu-gebonden zijn en er in eerste instantie vanuit de mantelzorger meestal geen vraag is om de huidige situatie te veranderen, ondanks de problematieken. Cfr. status quo bias.

### Case 2 – André Verschaffel

Omwille van de verwardheid en de emotionele onrust bij bij André, werden geen testen met zijn participatie uitgevoerd. De installatie van de prototypes in de omging legden desalniettemin enkele problemen bloot.
- De pendellamp blijft niet stilhangen en zal voor onnodige afleiding zorgen.
- De lichtintensiteit van de verschillende functies moeten worden afgesteld o.b.v. doel en o.b.v. omgevingslicht.
- De lichten mogen nooit direct in de ogen schijnen.
- De fade-in en fade-out effecten moeten zeer geleidelijk aan gebeuren om geen agitatie te veroorzaken.
- Wat met deuren die blijven opstaan?

Gebruiksgericht ontwerpen Viktor Fabry Elias Verdegem 2024 – 2025 | 5

### Case 3 – Andrea Vansteenkiste

Bevindingen na Test 3

De derde test werd uitgevoerd bij Andrea, een oudere zonder dementie, om een baseline te vormen voor toekomstige toepassingen bij licht-dementerenden. De test bood inzichten in de effectiviteit van verschillende interventies en de toepasbaarheid van het systeem bij niet-demente ouderen.

Feedback en Observaties:

- Slaapomgeving:
De kamer was verduisterd en voorzien van een bewegingsdetectielampje. Dit lampje was uitgezet tijdens de test. De beacon was tegen de muur opgesteld, maar de verlichting was onvoldoende gericht op het bed. Andrea stelde voor om rondom het bed meer verlichting te voorzien voor betere zichtbaarheid.
- Verlichting:
- Nightsky-verlichting: Andrea ervaarde de verlichting als neutraal. Meer variatie in kleuren en beweging kan bijdragen aan een betere evaluatie.
- Wekker met blauw licht en vogelgeluiden: Dit werd zeer positief ontvangen. De combinatie van licht en geluid had een nostalgisch effect en hielp bij een rustige start van de dag.
- Alarm met rood licht en geluid: Hoewel effectief, gaf het rode licht een rustgevende sfeer in plaats van urgentie. Knipperende lichten (ICE) kunnen mogelijk beter functioneren.
- Geluid:
Het rustgevende geluid, zoals pink noise, werd als niet-storend ervaren. Echter, de nieuwsgierigheid naar de herkomst van onbekende geluiden kan afleiden. Een betere studie naar nieuwsgierigheid en rust kan een optie zijn.
- Bewegwijzering:
De breadcrumbs werden tijdens de test niet opgemerkt, mogelijk vanwege hun hoogte. Dit kan ook komen doordat Andrea semi-onbewust naar het toilet loopt. Suggestie: nachtelijke tests uitvoeren met mensen met dementie om de effectiviteit beter te beoordelen.
- Geurtherapie:
Andrea stond positief tegenover geurtherapie. Ze merkte op dat een aangename geur een subtiel positief effect heeft op het gevoel.

Aanbevelingen Test 3:

- Verbeter de spotverlichting rondom het bed om betere zichtbaarheid te creëren.
- Varieer in kleur en beweging bij nightsky-verlichting voor een uitgebreidere evaluatie.
- Overweeg knipperende rode lichten (ICE) voor alarmmeldingen.
- Test bewegwijzering in situaties met personen met dementie om gebruik in een nachtelijke context beter te begrijpen.
- Integreer geurtherapie subtiel in het systeem om positieve effecten te benutten.

Algemene Conclusies uit alle Tests:

Een van de belangrijkste zaken uit de tests is dat de producten zeker niet te invasief mogen zijn, het stigma en ontkenning van de ziekte loopt vaak in het gedrang met het product. Het doel is om enerzijds het product deel te laten maken van het interieur, en anderzijds reeds in gebruik is vooraleer de personen in verdere stadium van de ziekte zitten. De derde test bevestigde dat interventies, zoals verlichting, geluid en geurtherapie, ook waardevol kunnen zijn voor ouderen zonder dementie. Deze resultaten dienen als baseline voor toekomstige tests bij mensen met beginnende dementie.

- Gepersonaliseerde en intuïtieve ontwerpen verhogen de effectiviteit en acceptatie van hulpmiddelen.
- Differentiatie in oplossingen op basis van cognitieve en fysieke behoeften blijft essentieel.
- Integratie in bestaande woonomgevingen moet subtiel en gebruiksvriendelijk zijn.

Deze inzichten vormen een solide basis voor verdere productontwikkeling en optimalisatie.

De grootste focus bij het product zou liggen bij gebruik van variatie van bewegend licht, geur en –met oplettend voor nieuwsgierigheid- geluid. De ‘knuffel’ zal achter wege gelaten worden, deels omdat de markt hier al vol van is, en uit de testen deze neutraal of niet geïmplementeerd waren.

Gebruiksgericht ontwerpen Viktor Fabry Elias Verdegem 2024 – 2025 | 6

## Conclusie

### Bevindingen m.b.t. de verdere evaluatie van het product

Voor de verdere testen zijn volgende aandachtspunten mee te nemen:
- Een zorgvuldige selectie van de testpersonen (stadium van de ziekte en aard van de problematiek). Bij testpersonen in een vroeg stadium van de ziekte is de emotionele impact kleiner en zijn de communicatieve mogelijkheden groter.
- Een vooraf geïnformeerde en persoonsgebonden aanpak per testcase.
- Een zo realistisch mogelijk testscenario met een minimum aan externe prikkels. Een ideaal scenario is een werkelijke nacht, zonder merkbare observatie met een correct werkende minimal viable product prototype. Er ontbraken enkele cruciale functionaliteiten (spraakboodschap), terwijl andere functionaliteiten door sommige testpersonen als posities en anderen net heel storend werden ervaren. Enkele afstellingen zijn noodzakelijk. Individuele instelbaarheid komt telkens naar voren. Positionering en (on)zichtbaarheid zijn belangrijke onderzoeksvragen.

## Implicaties

### Bevindingen m.b.t. de functionaliteiten

- Spraakfunctie “het is nog nacht” (evt. sprekende klok) is wenselijk als optie.
- Waarschuwingsfunctie met instelbare tijdgevoeligheid is wenselijk.
- Koppeling met DECT van PZ in WZC
- Koppeling met smartphone MZ en IZ
- Functies die niet noodzakelijk of wenselijk zijn mogen niet worden opgedrongen. Het product moet voldoende instelbaar zijn, op een laagdrempelige manier.
- Het product mag in geen geval een gevoel van schaamte veroorzaken. Aandacht voor confrontatie met de ziekte.
- De lichtintensiteit van de verschillende functies moeten worden afgesteld op basis van doel en omgevingslicht.
- De lichten mogen nooit direct in de ogen schijnen.
- De fade-in en fade-out effecten moeten zeer geleidelijk aan gebeuren om geen agitatie te veroorzaken.
- Prikkels moeten voldoende subtiel, doch merkbaar zijn (nudging).
- De wayfinding moet functioneren, ook wanneer de deuren die blijven opstaan.
- Belang van de timing van de introductie van een hulpmiddel in een vroeg stadium.

### Bevindingen m.b.t. de vorm en uitvoering

- Plaats de beacon buiten het onmiddellijke bereik van de PwD om afleiding te vermijden.
- De plafondinstallatie van de beacon is niet in elke context mogelijk en veroorzaakt storend en afleidend slingeren.
- De breadcrumb moet ook op schuifdeuren geïnstalleerd kunnen worden.
- De breadcrumb dient op te gaan in hun omgeving.
- Bijvoorbeeld door het buiten het zichtveld te plaatsen.
- Bijvoorbeeld door het als een herkenbaar ding te ‘vermommen’, dan wel het effectief te zijn.
- Te onderzoeken of de breadcrumb niet eerder de positie van de lichtschakelaar dan van de deurklink moet innemen?
- Overweeg hoe het product zou kunnen worden ‘vermomd’ als een gewoon dagdagelijks toestel
- Breadcrumb als lichtschakelaar (of op de plaats van)
- Breadcrumb op hoogte, buiten het direct zichtsveld
- Beacon als nachtlamp of als wandlamp
- Een emotioneel / nostalgische waarde zou de acceptatie kunnen vergemakkelijken.
- Pwd zou de kans kunnen krijgen om de functies zelf gaandeweg te ontdekken (goal gradient, fluency heuristic) om acceptatie te bevorderen.

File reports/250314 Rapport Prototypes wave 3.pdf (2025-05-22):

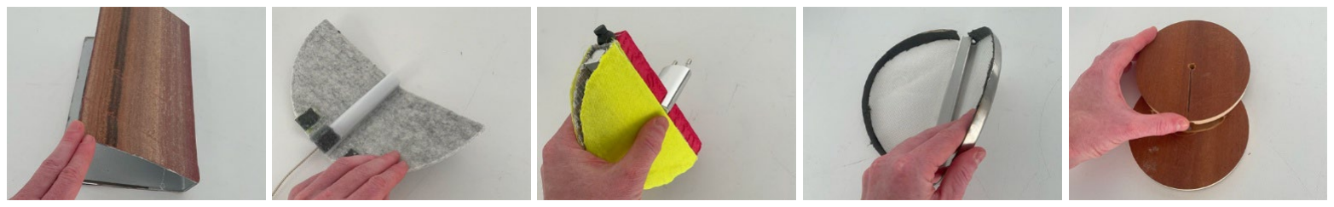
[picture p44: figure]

Gebruiksgericht ontwerpen Viktor Fabry Elias Verdegem 2024 – 2025 | 1
Prototypes wave 3 | Rapport
Hulpmiddel voor mantelzorgers van personen met dementie (werktitel) | 14/03/2025

## Projectinformatie

Project: Een oplossing ter bevordering van de slaap van personen met dementie met een verstoord dag-nacht-ritme en hun mantelzorgers.
Interviewers: Elias Verdegem & Viktor Fabry, studenten industrieel ontwerpen – opdracht gebruiksgericht ontwerpen

## Onderzoeksdoel

Deze derde testgolf richtte zich op de visuele en conceptuele evaluatie van verschillende prototypes. Er werd bewust geen functionele werking getest. De focus lag op de esthetische, emotionele en intuïtieve indrukken die de prototypes opwekten, aangevuld met gesprekken over verwachte interactie, plaatsing, activatie en scenario-gebruik.

## Methodes

- BERT-testing: gericht op esthetische en emotionele evaluatie van CMF (Color, Material, Finish)
- Semi-gestructureerde interviews: feedback op gebruiksvriendelijkheid, plaatsing, en verwachte werking
- SAM-tests werden voorzien maar uiteindelijk niet afgenomen.

## Prototypes

De volgende varianten werden getest op CMF, gebruiksgemak en signaalwaarde:
Boek | Vlinder | Discobal | Schelp | Pacman

## Steekproefomschrijving (N = 12)

De testen werden uitgevoerd met respondenten uit drie doelgroepen:
- Ouders met jonge kinderen (N = 4)
- Personen rond de pensioenleeftijd (N = 4)
- Ouderen van 75+ (N = 4)

## Protocol

250303 Protocol Prototypes wave 3.pdf (https://ugentbe-my.sharepoint.com/:b:/g/personal/elias_verdegem_ugent_be/EQc9bVL98C1Bg9wy_j9wrJwBJp-GJjBEg8ULPVaeS8YLjg?e=jxZeRa)

Gebruiksgericht ontwerpen Viktor Fabry Elias Verdegem 2024 – 2025 | 2

## Bevindingen per thema

### Vormgeving & Materiaalkeuze (CMF)

- Opvallende ontwerpen met felle kleuren en glanzende afwerkingen werden geapprecieerd door kinderen, maar stuitten op weerstand bij volwassenen.
- Volwassen respondenten verkiezen sobere, minder opvallende ontwerpen die rust uitstralen en niet technisch ogen.
- Houten en metalen materialen werden positief beoordeeld, vooral door het oudere publiek.
- Stoffen oppervlakken werden als onaantrekkelijk en vuilgevoelig beschouwd, zeker bij gezinnen met jonge kinderen.
- De voorkeur ging naar materialen die duurzaam én eenvoudig schoon te maken zijn.

### Context & Plaatsing

- Lichtgebruik in de slaapkamer moet tot een minimum beperkt worden, zeker voor mensen met slaapproblemen.
- Een subtiele lichtprojectie (bv. een lichtpuntje) wordt als mogelijke oplossing gezien in de slaapkamer.
- In de gang wordt licht minder problematisch ervaren, maar fel licht kan tot nachtblindheid leiden.
- Een deur op een kier met licht uit het toilet of de badkamer kan voldoende zijn en is minder storend dan gangverlichting.
- Licht dat geprojecteerd wordt (zoals een lijn op de vloer) moet nog getest worden op zichtbaarheid vanuit verschillende hoogtes.
- Ouders gaven de voorkeur aan draadloze toestellen omdat er vaak geen geschikte stopcontacten beschikbaar zijn voor plaatsing op de ideale plek.
- Ingebouwde verlichting wordt als veiliger en esthetisch beter bevonden.

### Gebruiksgemak & Verwachtingen

- Ouderen van 75+ toonden een sterke voorkeur voor bediening met slechts één knop (aan/uit), zonder uitleg of instellingen.
- Personen rond de pensioenleeftijd waardeerden duidelijke signifiers zoals knoppen of fysieke vormen, en gaven aan belang te hechten aan autonomie en controle over licht en geluid.
- Simpele en sobere ontwerpen werden algemeen als positief ervaren.
- Ouderen hadden meer moeite met automatische of onduidelijke functies, wat wijst op de nood aan eenvoudige, voorspelbare interacties.
- Het pacman-prototype werd gewaardeerd om zijn eenvoud, herkenbaarheid en discrete plaatsing vlak tegen de muur.

### Cognitieve & Emotionele Reacties

- Kinderen begrijpen abstracte concepten (zoals dag/nacht aangeduid via kleur) als ze worden uitgelegd, maar verliezen snel interesse na een paar keer.
- Bij personen met dementie werkt uitleg enkel in de beginfase; daarna moet het product zonder uitleg intuïtief blijven.
- Personen met dementie hebben de neiging om automatische verlichting handmatig uit te willen schakelen, wat verwarring kan veroorzaken.
- Kinderen zijn gevoeliger voor subtiele prikkels dan ouderen, bij wie visuele signalen soms minder snel worden opgemerkt.
- De positie van het lichtsignaal is belangrijker voor ouderen dan voor kinderen, aangezien ouderen meestal recht vooruit of naar beneden kijken.
- Kinderen scannen spontaan hun hele omgeving en zijn daardoor minder afhankelijk van de exacte plaatsing.
- Voor kinderen kan het systeem nuttig zijn in tijdelijke omgevingen zoals opvang, ziekenhuis, bij de babysit of op kamp.
- Licht in de kamer kan voor een kind het signaal zijn dat het terug naar bed mag.
- Een stem kan bij jonge kinderen rustgevend zijn bij het inslapen, maar wordt voor ouderen als desoriënterend ervaren.
- Een lamp die achter de toiletdeur licht geeft kan kinderen geruststellen die bang zijn in het donker.
- Ronde vormen riepen bij sommigen associaties op met een kattenoog (schelp en discobal) en werden minder goed onthaald.

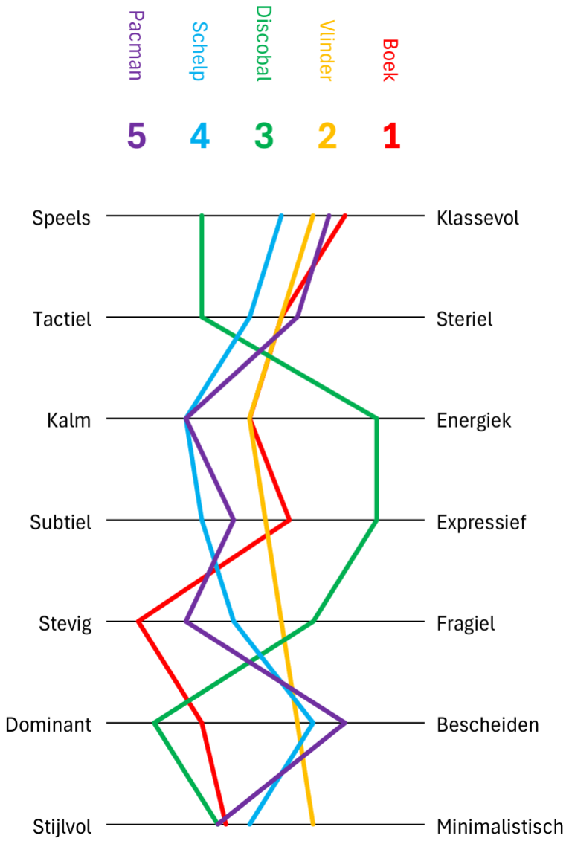
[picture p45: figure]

Gebruiksgericht ontwerpen Viktor Fabry Elias Verdegem 2024 – 2025 | 3

## Resultaten van de BERT-testing

Discobal (groen, 3)
scoort het meest expressief, energiek en speels, maar ook dominant en minder subtiel. Deze eigenschappen sluiten aan bij de voorkeur van kinderen, maar zijn minder geschikt voor volwassen of oudere gebruikers die rust en subtiliteit verkiezen.
Boek (rood, 1) en Vlinder (geel, 2)
worden als meer klassevol, subtiel en stijlvol ervaren, met de Boek-variant als de meest stevige en de Vlinder als het meest minimalistisch. Deze scores passen goed bij de voorkeuren van volwassenen en ouderen die op zoek zijn naar rustige, niet-opdringerige objecten.
Pacman (paars, 5)
combineert bescheidenheid, kalmte en stijlvolheid met een zekere tactiele aantrekkelijkheid. Deze balans verklaart waarom deze variant geliefd was bij de pensioenleeftijdsgroep. De herkenbaarheid en rustige uitstraling zorgen voor een gevoel van comfort zonder te overweldigen.
Schelp (blauw, 4)
scoort opvallend hoog op klassevol en speelsheid, wat een interessante mix vormt, maar heeft een minder uitgesproken profiel op andere assen. Dit wijst op een neutrale tot positieve algemene indruk, zonder sterke pieken of dalen.

## Conclusie

De testresultaten tonen aan dat de visuele subtiliteit, materialiteit en flexibiliteit van het ontwerp essentieel zijn voor brede aanvaardbaarheid. Vooral bij ouderen is er een nood aan intuïtieve, niet-opdringerige oplossingen die rust uitstralen en passen binnen het bestaande interieur. Dit vraagt om een verschuiving van ‘functionele gadgets’ naar vertrouwde, integreerbare objecten. De volgende ontwikkelingsfase moet inzetten op minimalistische vormgeving, zachte signalen en contextafhankelijke activatie, met duidelijke differentiatie per doelgroep. Deze inzichten sturen het product richting een laagdrempelige, verplaatsbare en visueel aanvaardbare nachtelijke assistent, bruikbaar zowel thuis als in tijdelijke situaties zoals logeerpartijen of ziekenhuisopnames.

## Implicaties (PDR)

Het product moet:
- Draadloos zijn en vrij plaatsbaar zonder afhankelijkheid van stopcontacten
- Zacht en subtiel licht geven dat de slaap niet verstoort
- Scheiding mogelijk maken tussen ‘licht geven’ en ‘aandacht trekken’
- Eenvoudige visuele en/of auditieve prikkels bieden, afhankelijk van de doelgroep
- Bestaan uit kwalitatieve, onderhoudsvriendelijke materialen zoals hout, metaal of plastic

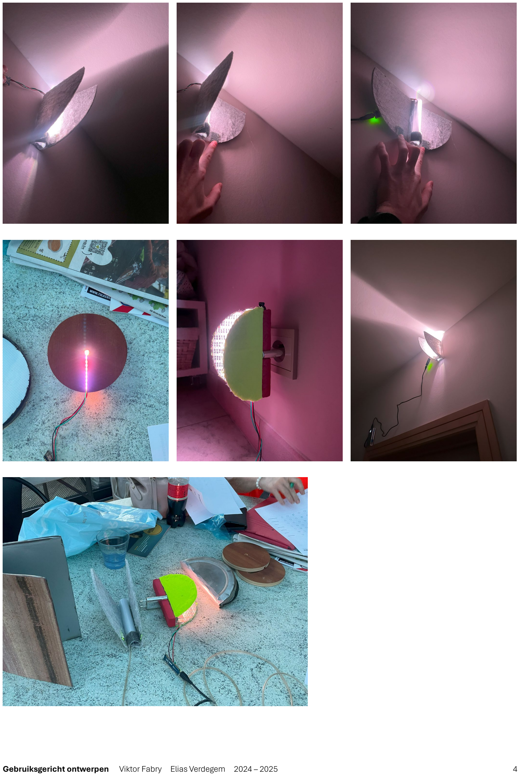
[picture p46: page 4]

Gebruiksgericht ontwerpen Viktor Fabry Elias Verdegem 2024 – 2025 | 4

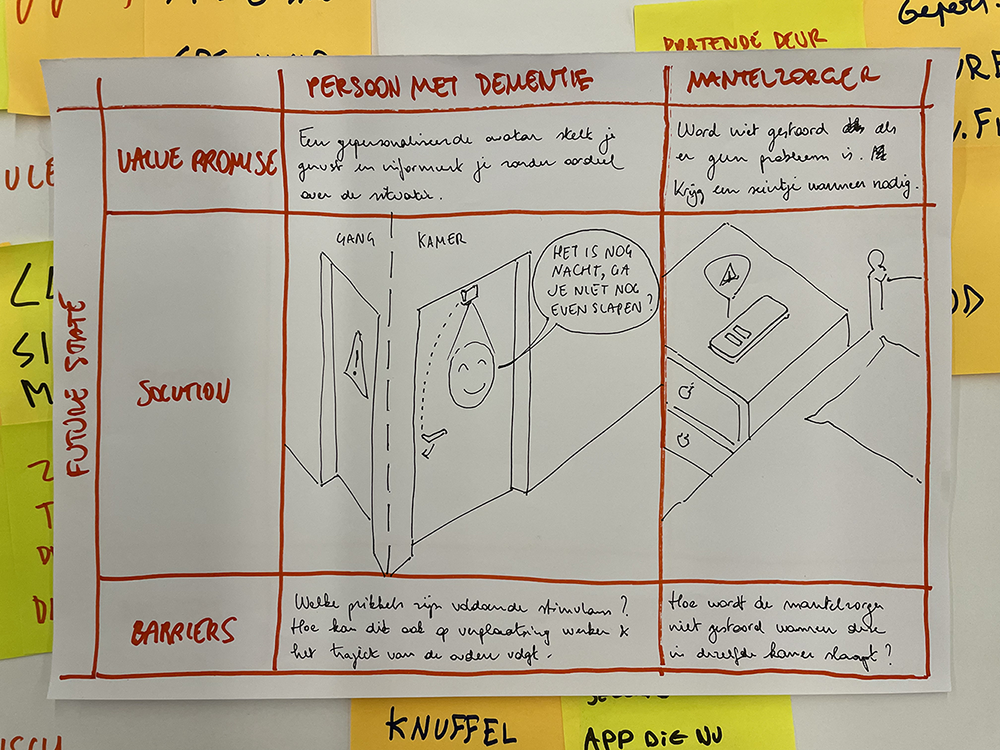
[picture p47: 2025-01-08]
img/Design sprint innovatrix.png

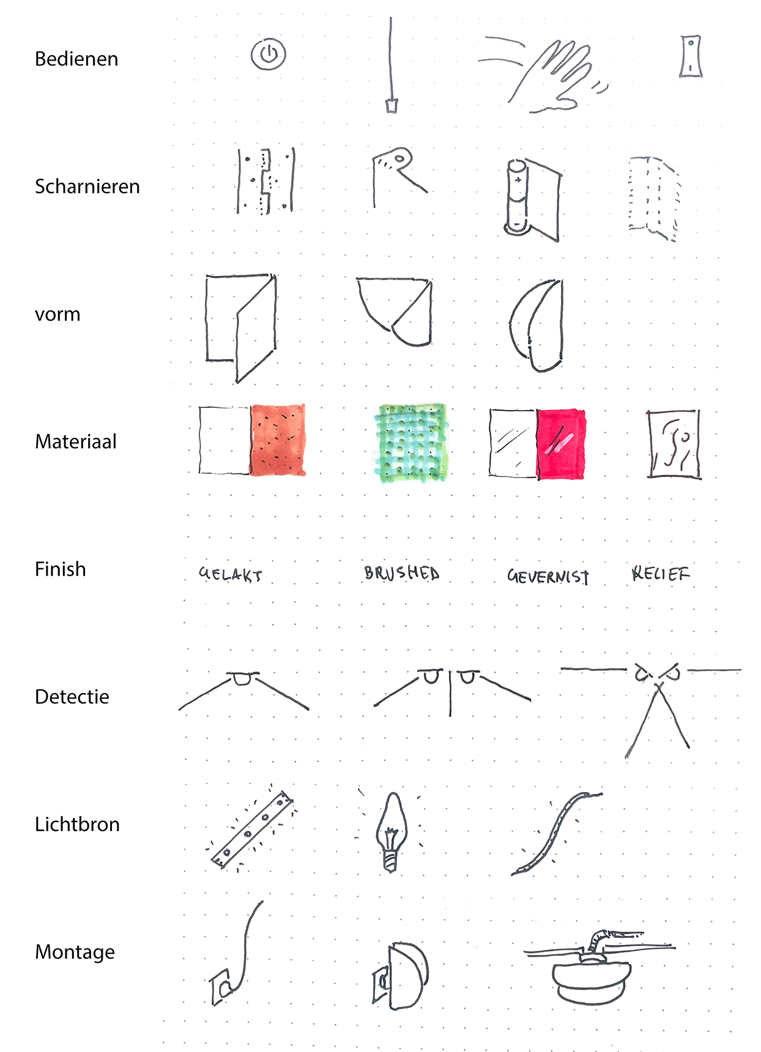
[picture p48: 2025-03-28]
img/Prototypes morfologische matrix.png

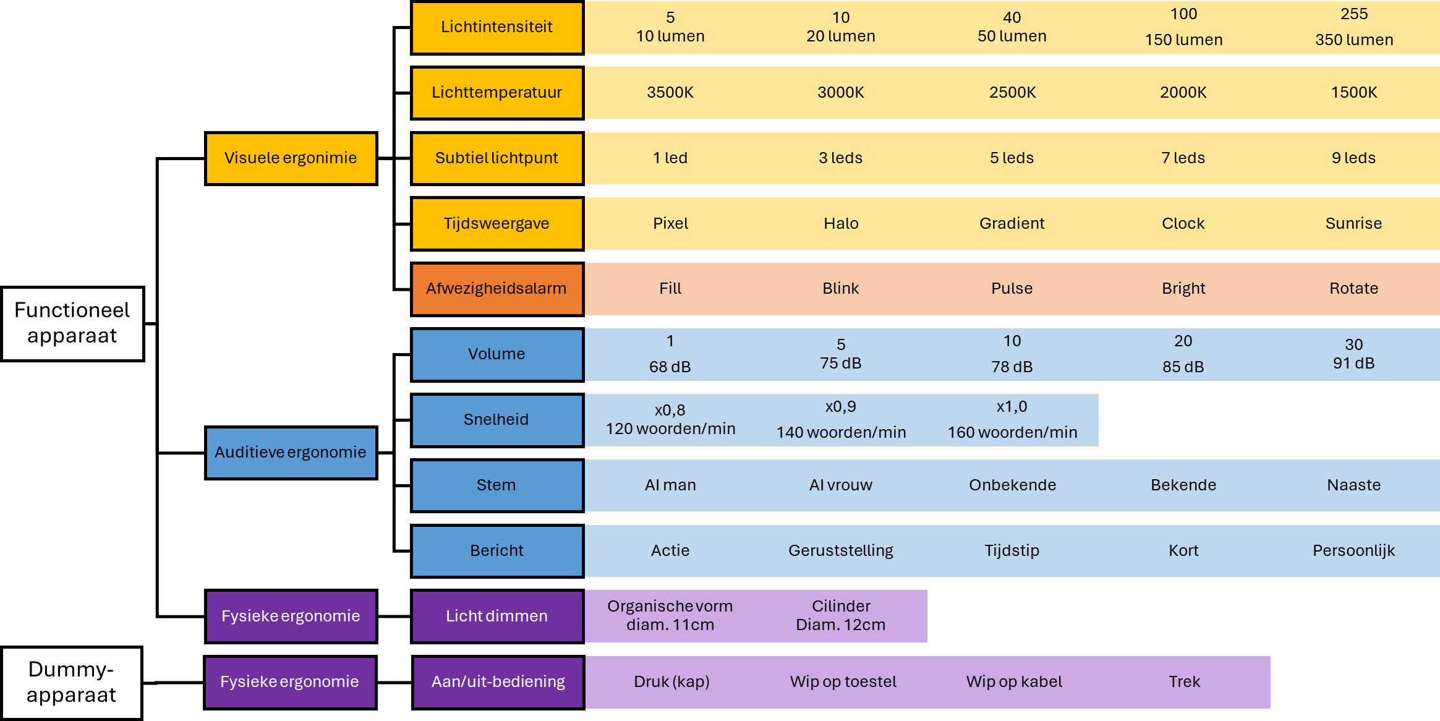
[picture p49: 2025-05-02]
img/Prototypes UI options.png

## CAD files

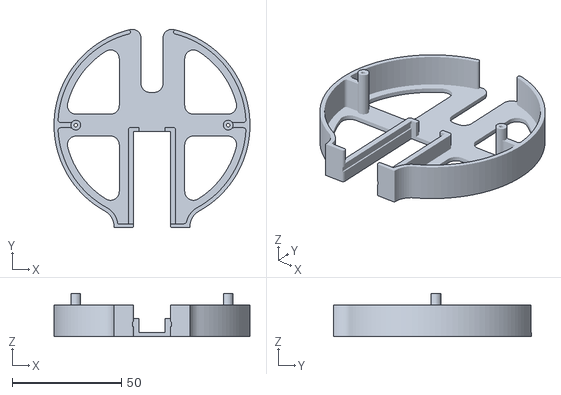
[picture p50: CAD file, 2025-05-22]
cad/pasvorm 2.stl
89.8 x 90.9 x 19.8

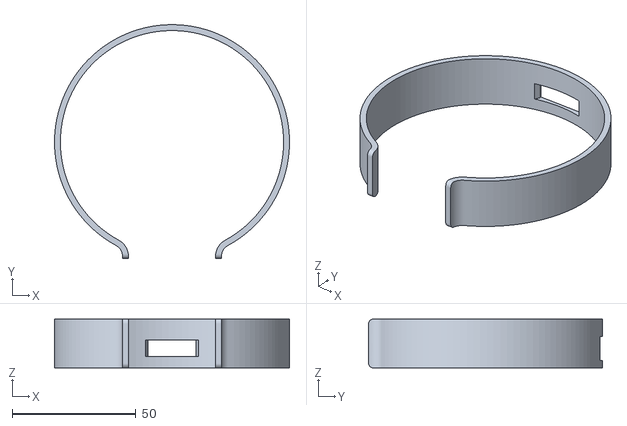
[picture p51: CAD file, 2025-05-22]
cad/rand.stl
95.0 x 94.5 x 19.8

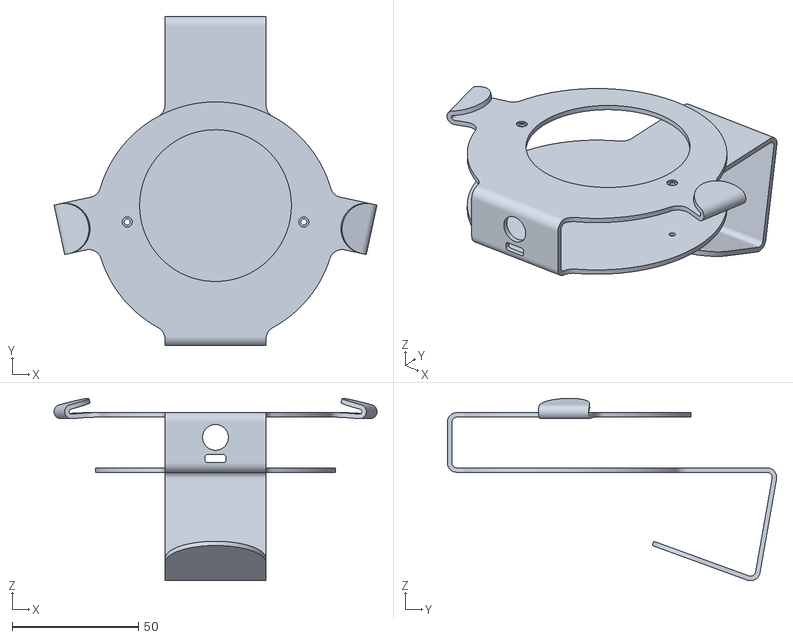
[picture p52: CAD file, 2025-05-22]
cad/haak.stl
127.7 x 130.2 x 72.1

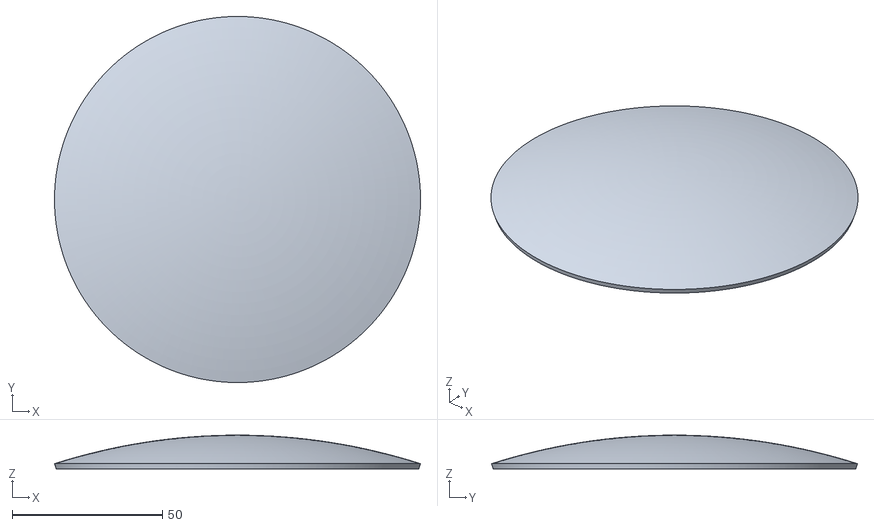
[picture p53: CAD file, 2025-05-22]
cad/schijf.stl
122.0 x 122.0 x 11.2

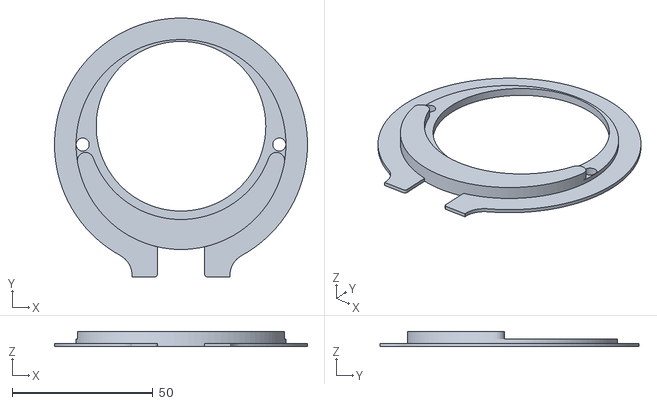
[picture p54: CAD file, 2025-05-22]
cad/pasvorm 1.stl
89.8 x 91.9 x 5.50

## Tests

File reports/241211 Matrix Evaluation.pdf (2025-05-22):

# Matrix evaluation

## Functions

Feature | Master | Slave | Peripheral (optional)
Wayfinding voor PD | +++ | ++++ | ++
Kalmerend/geruststellend voor PD | ++++ | ++ | ++
Geruststellend voor MZ | +++ | + | +
Detectie onrust PD | ++ | + | +++
Must ++++ | Should +++ | Could ++ | Would +

## Beacon (master)

Variants

Vorm | Plaats | Voordelen | Nadelen
Vaste pendelmodule Vaste wandmodule | Boven nachtkussen Boven bedhoofdeinde | + signaal thv kussen + netstroom/batterij + altijd correcte positie | - afleidend - installatie
Draagbare module | Op nachtkast | + eenvoudige installatie + netstroom/batterij | - richtbaarheid
Kussen | In bed | + signaal thv kussen | - brandveiligheid
Knuffel | In of naast bed | + signaal thv bed + afwezigheidsdetectie | - kinds
Wearable horloge Wearable huisticker (optional peripheral) | Rond de pols Op borstkas | + onrustdetectie + slaapdetectie + valdetectie | - vergeten aandoen - storend - oplaadfrequentie

Internals

Feature | Action | 1 | 2 | 3 | 4
Geur | Nacht: Lavendel/Kamille/... Ochtend: Koffie/Citrus/Eucalyptus/... | Ultrasone verstuiver (Piezo) | Hittespoel verdamper | Luchtdruk vernevelaar
Geluid | Pink noise Muziek Luisterverhaal Herkenbare stem | Buzzer | Passieve speaker | Versterkte speaker
Detectie | Monitoring op afstand Afwezigheidsdetectie Slaapdetectie | PIR + IR reflectie | IR camera | Radar | Thermische camera
Licht | Wayfinding
Wekker

RGB LED LED per
kleur

LED filament

Feature | Action | 1 | 2 | 3 | 4
| Alarmering Snoezel
Communicatie | Aansturen breadcrumbs | IR | Zigbee (https://docs.arduino.cc/retired/shields/arduino-xbee-shield/) | BLE
Communicatie | Instelling via smartphone-app | Wifi | Zigbee (https://docs.arduino.cc/retired/shields/arduino-xbee-shield/) | BLE

Externals (ntb)

Nog te ontwerpen

## Breadcrumb (slave)

Variants

Vorm | Plaats | Voordelen | Nadelen
Klink | In plaats van de klink | + geïntegreerd | - installatie - schuifdeuren
Klinksleeve | Over het klinkhandvat | + nomadisch + non-destructief | - integratie van tech - compatibiliteit - duurzaamheid
Klinkring | Over de klinkas | + nomadisch | - compatibiliteit
Pod | Op deurblad of wand | + multi-inzetbaar | - schroeven/lijmen
Deurklem | Over deurblad | + 2-zijdig + universeel | - enkel bij deur

Internals

Feature | 1 | 2 | 3 | 4 | 5
Detectie | Geen | Ultrasoon | PIR | Radar | Biometrie
Communicatie | IR | BLE | Wifi | Zigbee (https://docs.arduino.cc/retired/shields/arduino-xbee-shield/) | LoRa
Licht | X# LEDs | LED stick | LED filament | LED strip
Secundaire trigger | Geen | Acceleratiemeter | Klinkdetectie | dB-meter
Secundaire controller | Geen | Lichtsensor | Timer
Bediening | Geen | Aan/uit-knop | Uitknop | Dimknop
Voeding | Netstroom | Vervangbare batterij | Oplaadbare batterij | Dynamo

Externals (ntb)

Nog te ontwerpen

Feature | 1 | 2 | 3 | 4 | 5 | 6
Lichtdiffuser
Bevestiging | Vast geschroefd | Vast gelijmd | Magneet | Schuifsleuf | Draaisleuf | Klikveer
Bevestiging houder | Geen | Geschroefd | Gelijmd | Velcro | Rubber | Klem

Feature | 1 | 2 | 3 | 4 | 5 | 6
Behuizing CMF

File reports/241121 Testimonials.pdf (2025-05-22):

# Testimonials

Jorick Cappon

Een verstoorde nachtrust van personen met dementie is vaak hert duwtje van dagopvang naar vaste opvang.

Dementie Anders Beleven | Facebook (https://www.facebook.com/groups/1463081801153845/permalink/1748109309317758/)

Doordat veel ouderen overdag te weinig rust krijgen, zijn ze aan het eind van de dag uitgeteld. Het gedrag van veel ouderen met dementie verandert dan. Ze worden rustelozer, willen naar huis of naar hun ouders, gaan rondlopen, zijn moeilijk gerust te stellen, verwarder en onsamenhangender. Het zogenaamde ‘Sundowning syndroom’.

Dementie Anders Beleven | Er verblijft sinds kort een dame in een WZC die elke avond op zoek gaat naar haar
huis | Facebook (https://www.facebook.com/groups/1463081801153845/permalink/1668655500596473/)

Q Er verblijft sinds kort een dame in een WZC die elke avond op zoek gaat naar haar huis. Ze gaat andere kamers binnen, kruipt in andermans bed, zit aan persoonlijke spullen van anderen en verstoort de rust van medebewoners waardoor zij allen geagiteerd raken.
A Stickers op haar deur: aan de binnenzijde met een raam zodat ze niet ziet dat het een deur is. Aan de buitenzijde een herkenbare deur. Vraag aan de kinderen of ze een foto hebben van de voordeur van haar vroeger huis en of ze daar een deursticker van willen laten maken.
A We hadden ook een dame met dit probleem. Die doolde wel niet maar ik liet haar dan naar haar dochter bellen. Daarna was ze rustiger.
A Wij gaan ‘s avonds bij valavond even wandelen in onze tuin met onze dolende bewoners. Dit is vaak maar 20’, maar geeft zoveel rust aan de dolende bewoner en de andere bewoners.
A Hier hebben we de foto’s van de kleinzonen aan haar deur gehangen zodat ze deze herkend.
A Verzwaardeken, verzwaarpop of knuffel.
A Zeg niet, dat is uw kamer niet, maar probeer de mogelijke reden te begrijpen. Wat is het gedrag? iemand met dementie loopt kamers van medebewoners binnen. Wat zit erachter dit gedrag? Ze is zoekende. Waar is de persoon met dementie naar op zoek? Is het veiligheid, herkenning? Wat voor emotie zou iemand kunnen voelen op dit moment? Angst, verdriet? Desoriëntatie in plaats is een veel voorkomend symptoom, je voelt je altijd vreemd in de omgeving en bent door de dementie niet in staat de nieuwe omgeving op te slaan. Dus niet corrigeren: "Dit is jouw kamer niet", maar wel: "Ben je iets aan het zoeken? Kan ik je helpen?". Je gebruikt best vertrouwde bezittelijke voornaamwoorden, zoals "je" en "jouw" en niet "uw", omdat het gelijkwaardig en persoonlijker is in omgang en de persoon met dementie zich misschien als veel jonger ziet.

Aromatherapie vermindert onrust bij ernstige dementie - Innovatiekring Dementie (https://www.innovatiekringdementie.nl/a-155/aromatherapie-vermindert-onrust-bij-ernstige-dementie/index.html)

Het kruid Melissa vermindert onrust bij mensen met ernstige dementie. Dat blijkt uit onderzoek in Engeland. Ook leidt deze zogenoemde 'aromatherapie' tot minder sociale teruggetrokkenheid.

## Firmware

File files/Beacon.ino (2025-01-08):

#include <IRremote.h>
#include <FastLED.h>

// ====================
// CONFIGURATIONS
// ====================

// IR Remote Setup
#define IR_RECEIVE_PIN 2
#define REMOTE_1 0xC03F5583     // NEC code for button 1
#define REMOTE_3 0xDC235583     // NEC code for button 3
#define REMOTE_4 0xBC435583     // NEC code for button 4
#define REMOTE_5 0xBE415583     // NEC code for button 5
#define REMOTE_6 0x9F605583     // NEC code for button 6
#define REMOTE_9 0x708F5583     // NEC code for button 9
#define REMOTE_ESC 0x7B845583   // NEC code for ESC button

// RGB LED Setup (Single LED)
#define RED_PIN 5
#define GREEN_PIN 10
#define BLUE_PIN 6
const int rgbPins[] = {RED_PIN, GREEN_PIN, BLUE_PIN};
const int rgbValues[] = {200, 50, 0};
const int maxBrightness = 255;

// RGB Addressable LEDs
#define LED_PIN 9
#define NUM_LEDS 10
#define LED_BRIGHTNESS 255
CRGB leds[NUM_LEDS];
CRGB nextLeds[NUM_LEDS];
CRGB currentLeds[NUM_LEDS];

// State Control
bool pillowActive = false;
bool skyActive = false;
bool alarmActive = false;
bool singleRGBActive = false;
bool stopSunrise = false;
bool fadeOutSunrise = false;
bool breathingActive = false;
float currentBrightness = 0.0;

const unsigned long delayInterval = 10;
const unsigned long fadeStepInterval = 50;
int currentFadeStep = 0;
unsigned long lastFadeMillis = 0;

// ====================
// FUNCTIONS
// ====================

// ===== Helper Functions =====
void fadeDownToBlack() {
  float fadeBrightness = currentBrightness;
  while (fadeBrightness > 0.01) {
    fadeBrightness -= 0.01;
    for (int i = 0; i < 3; i++) {
      analogWrite(rgbPins[i], (rgbValues[i] * fadeBrightness));
    }
    delay(delayInterval);
  }
  for (int i = 0; i < 3; i++) analogWrite(rgbPins[i], 0);
  Serial.println("Single RGB LED Faded Out");
}

void fadeUpToBlack() {
  for (int fadeStep = 0; fadeStep <= 255; fadeStep += 5) {
    for (int i = 0; i < NUM_LEDS; i++) {
      leds[i].fadeToBlackBy(5);
    }
    FastLED.show();
    delay(20);
  }
  FastLED.clear();
  FastLED.show();
  Serial.println("LED Strip Faded Out");
}

void stopAllEffects() {
  if (singleRGBActive) fadeDownToBlack();
  if (skyActive || alarmActive || fadeOutSunrise || breathingActive) fadeUpToBlack();
  singleRGBActive = skyActive = alarmActive = fadeOutSunrise = breathingActive = false;
  stopSunrise = true;
}

// ===== Meditation effect =====
void Breathing() {
  Serial.println("Starting Breathing Exercise...");
  breathingActive = true;

  const int totalCycleTime = 10000;
  const int fadeInTime = 2000;
  const int fadeOutTime = 2000;
  const int holdTime = (totalCycleTime - fadeInTime - fadeOutTime) / 2;
  const int maxBrightness = 255;
  const int minBrightness = 90;

  bool firstCycle = true;

  while (breathingActive) {
    // Fade In
    int startBrightness = firstCycle ? 0 : minBrightness;
    for (int fade = startBrightness; fade <= maxBrightness; fade++) {
      fill_solid(leds, NUM_LEDS, CRGB::OrangeRed);
      FastLED.setBrightness(fade);
      FastLED.show();
      delay(fadeInTime / (maxBrightness - startBrightness));

      if (IrReceiver.decode()) {
        if (IrReceiver.decodedIRData.decodedRawData == REMOTE_ESC) {
          stopAllEffects();
          return;
        }
        IrReceiver.resume();
      }
    }

    // Hold at Full Brightness
    for (int i = 0; i < holdTime / 10; i++) {
      delay(10);
      if (IrReceiver.decode()) {
        if (IrReceiver.decodedIRData.decodedRawData == REMOTE_ESC) {
          stopAllEffects();
          return;
        }
        IrReceiver.resume();
      }
    }

    // Fade Out
    for (int fade = maxBrightness; fade >= minBrightness; fade--) {
      fill_solid(leds, NUM_LEDS, CRGB::OrangeRed);
      FastLED.setBrightness(fade);
      FastLED.show();
      delay(fadeOutTime / (maxBrightness - minBrightness));

      if (IrReceiver.decode()) {
        if (IrReceiver.decodedIRData.decodedRawData == REMOTE_ESC) {
          stopAllEffects();
          return;
        }
        IrReceiver.resume();
      }
    }

    // Hold at Low Brightness
    for (int i = 0; i < holdTime / 10; i++) {
      delay(10);
      if (IrReceiver.decode()) {
        if (IrReceiver.decodedIRData.decodedRawData == REMOTE_ESC) {
          stopAllEffects();
          return;
        }
        IrReceiver.resume();
      }
    }

    firstCycle = false;
  }

  Serial.println("Breathing Exercise Complete");
}

// ===== Beacon light =====
void Pillow() {
  pillowActive = true;
  singleRGBActive = true;
  currentBrightness = 0.0;
  unsigned long previousMillis = millis();

  while (currentBrightness <= 1.0 && pillowActive) {
    if (millis() - previousMillis >= delayInterval) {
      previousMillis = millis();
      currentBrightness = min(1.0, currentBrightness + 0.01);
      for (int i = 0; i < 3; i++) {
        analogWrite(rgbPins[i], (rgbValues[i] * currentBrightness));
      }
    }

    if (IrReceiver.decode()) {
      uint32_t irData = IrReceiver.decodedIRData.decodedRawData;
      if (irData == REMOTE_ESC) {
        stopAllEffects();
        return;
      }
      IrReceiver.resume();
    }
  }
  pillowActive = false;
  Serial.println("Fade-In Complete");
}

// ===== Sea Projection =====
void Sky() {
  Serial.println("Starting Sea Projection...");
  skyActive = true;
  currentFadeStep = 0;

  // Ensure LEDs start from off
  FastLED.clear();
  FastLED.show();

  // Set currentLeds to DarkBlue
  for (int i = 0; i < NUM_LEDS; i++) {
    currentLeds[i] = CRGB::DarkBlue;
  }

  // Fade In to DarkBlue
  for (int brightness = 0; brightness <= LED_BRIGHTNESS; brightness++) {
    fill_solid(leds, NUM_LEDS, CRGB::DarkBlue);
    FastLED.setBrightness(brightness);
    FastLED.show();
    delay(10);
  }
  Serial.println("Sea Projection Fade-In to DarkBlue Complete");

  // Run the projection effect
  while (skyActive) {
    if (millis() - lastFadeMillis >= fadeStepInterval) {
      lastFadeMillis = millis();
      for (int i = 0; i < NUM_LEDS; i++) {
        currentLeds[i].r += (nextLeds[i].r - currentLeds[i].r) / 8;
        currentLeds[i].g += (nextLeds[i].g - currentLeds[i].g) / 8;
        currentLeds[i].b += (nextLeds[i].b - currentLeds[i].b) / 8;
        leds[i] = currentLeds[i];
      }
      FastLED.show();

      if (++currentFadeStep >= 16) {
        currentFadeStep = 0;
        for (int i = 0; i < NUM_LEDS; i++) {
          int colorChoice = random(0, 4);
          nextLeds[i] = (colorChoice == 0) ? CRGB::Black :
                        (colorChoice == 1) ? CRGB::MediumBlue :
                        (colorChoice == 2) ? CRGB::DarkBlue : CRGB::DeepSkyBlue;
        }
      }
    }

    // Check for ESC signal
    if (IrReceiver.decode()) {
      if (IrReceiver.decodedIRData.decodedRawData == REMOTE_ESC) {
        stopAllEffects();
        return;
      }
      IrReceiver.resume();
    }
  }
  Serial.println("Sea Projection Stopped");
}

// ===== Sunrise Effect =====
void Sunrise() {
  Serial.println("Starting Sunrise Effect...");
  stopSunrise = false;
  fadeOutSunrise = false;
  float brightness = 0.0;
  for (int step = 0; step <= 1000 && !stopSunrise; step++) {
    brightness = pow((float)step / 1000, 2.2);
    for (int i = 0; i < NUM_LEDS; i++) {
      leds[i] = CRGB::White;
      leds[i].fadeToBlackBy(255 - (brightness * 255));
    }
    FastLED.show();
    delay(5);

    if (IrReceiver.decode()) {
      if (IrReceiver.decodedIRData.decodedRawData == REMOTE_ESC) {
        fadeOutSunrise = true;
        stopAllEffects();
        return;
      }
      IrReceiver.resume();
    }
  }
  Serial.println("Sunrise Complete");
  fadeOutSunrise = true;
}

// ===== Alarm Effect =====
void Alarm() {
  Serial.println("Starting Alarm Effect...");
  alarmActive = true;
  float brightness = 0.0;
  bool increasing = true;
  while (alarmActive) {
    brightness += (increasing) ? 0.003 : -0.003;
    increasing = (brightness >= 1.0 || brightness <= 0.0) ? !increasing : increasing;
    for (int i = 0; i < NUM_LEDS; i++) {
      leds[i] = CRGB::Red;
      leds[i].fadeToBlackBy(255 - (brightness * 255));
    }
    FastLED.show();
    delay(3);

    if (IrReceiver.decode()) {
      if (IrReceiver.decodedIRData.decodedRawData == REMOTE_ESC) {
        stopAllEffects();
        return;
      }
      IrReceiver.resume();
    }
  }
}

// ====================
// SETUP AND LOOP
// ====================
void setup() {
  Serial.begin(9600);
  IrReceiver.begin(IR_RECEIVE_PIN, DISABLE_LED_FEEDBACK);
  FastLED.addLeds<WS2812, LED_PIN, GRB>(leds, NUM_LEDS);
  FastLED.setBrightness(LED_BRIGHTNESS);
  Serial.println(F("IR Remote Ready - Waiting for Input"));
}

void loop() {
  if (IrReceiver.decode()) {
    switch (IrReceiver.decodedIRData.decodedRawData) {
      case REMOTE_1: Pillow(); break;
      case REMOTE_3: Breathing(); break;
      case REMOTE_5: Sky(); break;
      case REMOTE_6: Sunrise(); break;
      case REMOTE_9: Alarm(); break;
      case REMOTE_ESC: stopAllEffects(); break;
    }
    IrReceiver.resume();
  }
}

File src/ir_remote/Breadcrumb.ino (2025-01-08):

#include <IRremote.h>
#include <FastLED.h>

// IR codes
#define IR_RECEIVE_PIN 2
#define REMOTE_4 0xBC435583
#define REMOTE_7 0x619E5583

// LED strip
#define LED_PIN 9
#define NUM_LEDS 20
#define LED_BRIGHTNESS 150
CRGB leds[NUM_LEDS];
#define LED_COLOR CRGB(238, 153, 17)

// Flags
bool polestarActive = false;
float currentBrightness = 0.0;

// Helper functions

bool isStopSignalReceived() {
  if (IrReceiver.decode()) {
    if (IrReceiver.decodedIRData.decodedRawData == REMOTE_7) {
      Serial.println("STOP signal received (REMOTE_7)");
      stopAllEffects();
      return true;
    }
    IrReceiver.resume();
  }
  return false;
}

void stopAllEffects() {
  Serial.println("Stopping all effects and fading out.");
  fadeOutEffect();
  polestarActive = false;
  FastLED.clear();
  FastLED.show();
  currentBrightness = 0.0;
  delay(10);
}

void fadeOutEffect() {
  Serial.println("Fading out LEDs slowly.");
  for (int fadeStep = 0; fadeStep <= 255; fadeStep += 2) {
    for (int i = 0; i < NUM_LEDS; i++) {
      leds[i].fadeToBlackBy(2);
    }
    FastLED.show();
    delay(15); // Slower fade-out
  }
  FastLED.clear();
  FastLED.show();
}

// Actuator functions

void Polestar() {
  Serial.println("Starting Polestar effect.");
  polestarActive = true;
  float brightness = 0.0;

  for (int step = 0; step <= 1000 && polestarActive; step++) {
    brightness = pow((float)step / 1000, 2.2);
    for (int i = 0; i < NUM_LEDS; i++) {
      leds[i] = LED_COLOR;
      leds[i].fadeToBlackBy(255 - (brightness * 255));
    }
    FastLED.show();
    delay(3); // speed

    if (isStopSignalReceived()) {
      polestarActive = false;
      Serial.println("Fade-in interrupted by STOP signal.");
      return;
    }
  }

  Serial.println("Polestar effect complete.");
}

// Initial setup
void setup() {
  Serial.begin(9600);
  IrReceiver.begin(IR_RECEIVE_PIN, DISABLE_LED_FEEDBACK);
  FastLED.addLeds<WS2812, LED_PIN, GRB>(leds, NUM_LEDS);
  FastLED.setBrightness(LED_BRIGHTNESS);
  Serial.println(F("IR Remote Ready - Waiting for Input"));
}

// IR receiver
void loop() {
  if (IrReceiver.decode()) {
    Serial.print("IR code received: ");
    Serial.println(IrReceiver.decodedIRData.decodedRawData, HEX);
    switch (IrReceiver.decodedIRData.decodedRawData) {
      case REMOTE_4:
        Serial.println("REMOTE_4 detected - Starting Polestar.");
        Polestar();
        break;
      case REMOTE_7:
        Serial.println("REMOTE_7 detected - Stopping all effects.");
        stopAllEffects();
        break;
      default:
        Serial.println("Unknown IR code.");
        break;
    }
    IrReceiver.resume();
  }
}

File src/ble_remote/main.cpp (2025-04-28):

#include <Arduino.h>
#include <WiFiNINA.h>
#include <ArduinoBLE.h>
#include <WiFiServer.h>
#include <WiFiClient.h>
#include <Adafruit_NeoPixel.h>
#include <DFRobot_DF1201S.h>
#include "light.h"
#include "sound.h"
#include "scene.h"
#include <map>

// BLE service and characteristics
BLEService testService("0000180c-0000-1000-8000-00805f9b34fb");
BLEStringCharacteristic ssidCharacteristic("00002a57-0000-1000-8000-00805f9b34fb", BLEWrite, 128);
BLEStringCharacteristic passwordCharacteristic("00002a58-0000-1000-8000-00805f9b34fb", BLEWrite, 128);
BLEStringCharacteristic logCharacteristic("00002a59-0000-1000-8000-00805f9b34fb", BLERead | BLENotify, 512);

// Wi-Fi server
WiFiServer server(80);
bool wifiConnected = false;

// NeoPixel setup
#define LED_PIN 6
#define NUM_LEDS 24
Adafruit_NeoPixel strip(NUM_LEDS, LED_PIN, NEO_GRB + NEO_KHZ800);

// DFRobot DF1201S setup
DFRobot_DF1201S DF1201S;
#define DF1201S_SERIAL Serial1
#define DF1201S_BAUD 115200
bool df1201sInitialized = false;

// === Global variables for test interaction model ===
String currentTest = "";
int currentStep = 0;
String testLog = "";
std::map<String, String> testResults;

String getTestLabel(const String& test) {
  if (test == "A1") return "Intensity";
  if (test == "A2") return "Color";
  if (test == "A3") return "Focus";
  if (test == "A4") return "Time";
  if (test == "A5") return "Alarm";
  if (test == "B1") return "Volume";
  if (test == "B2") return "Speed";
  if (test == "B3") return "Voice";
  if (test == "B4") return "Message";
  return test;
}

String getTestValue(const String& test, int step) {
  if (test == "A1") {
    // Only reference values from light.cpp
    extern const int intensitiesA1[5];
    return String(intensitiesA1[step % 5]) + "/255";
  }
  if (test == "A2") {
    extern const char* colorTempsA2[5];
    return String(colorTempsA2[step % 5]);
  }
  if (test == "A3") {
    extern const int focusModesA3[5];
    return String(focusModesA3[step % 5]) + "/24 leds";
  }
  if (test == "A4") {
    extern const char* timeModesA4[5];
    return String(timeModesA4[step % 5]);
  }
  if (test == "A5") {
    extern const char* alarmModesA5[5];
    return String(alarmModesA5[step % 5]);
  }
  if (test == "B1") {
    extern const int volumesB1[5];
    return String(volumesB1[step % 5]) + "/30";
  }
  if (test == "B2") {
    extern const char* speedsB2[3];
    return String(speedsB2[step % 3]);
  }
  if (test == "B3") {
    extern const char* voicesB3[5];
    return String(voicesB3[step % 5]);
  }
  if (test == "B4") {
    extern const char* messagesB4[5];
    return String(messagesB4[step % 5]);
  }
  return String(step);
}

// === Helper functions for test interaction model ===
void runCurrentStep() {
  if (currentTest == "A1") {
    lightA1(strip, currentStep);
  } else if (currentTest == "A2") {
    lightA2(strip, currentStep);
  } else if (currentTest == "A3") {
    lightA3(strip, currentStep);
  } else if (currentTest == "A4") {
    lightA4(strip, currentStep);
  } else if (currentTest == "A5") {
    lightA5(strip, currentStep);
  } else if (currentTest == "B1") {
    soundB1(currentStep);
  } else if (currentTest == "B2") {
    soundB2(currentStep);
  } else if (currentTest == "B3") {
    soundB3(currentStep);
  } else if (currentTest == "B4") {
    soundB4(currentStep);
  }
}
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

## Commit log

2025-03-28 bill of materials.md
2025-04-24 arduino IoT UI
2025-05-02 materialen wave 4
2025-05-15 pilot prototype IoT stack
2025-05-22 conclusie en technische beschrijving
    [haak.stl, pasvorm 1.stl, pasvorm 2.stl, rand.stl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]
2025-05-22 3d print
2025-12-14 Fix links in README for Arduino and Raspberry Pi code
